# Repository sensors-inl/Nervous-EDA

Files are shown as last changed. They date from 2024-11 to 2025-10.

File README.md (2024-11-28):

<p align="center">
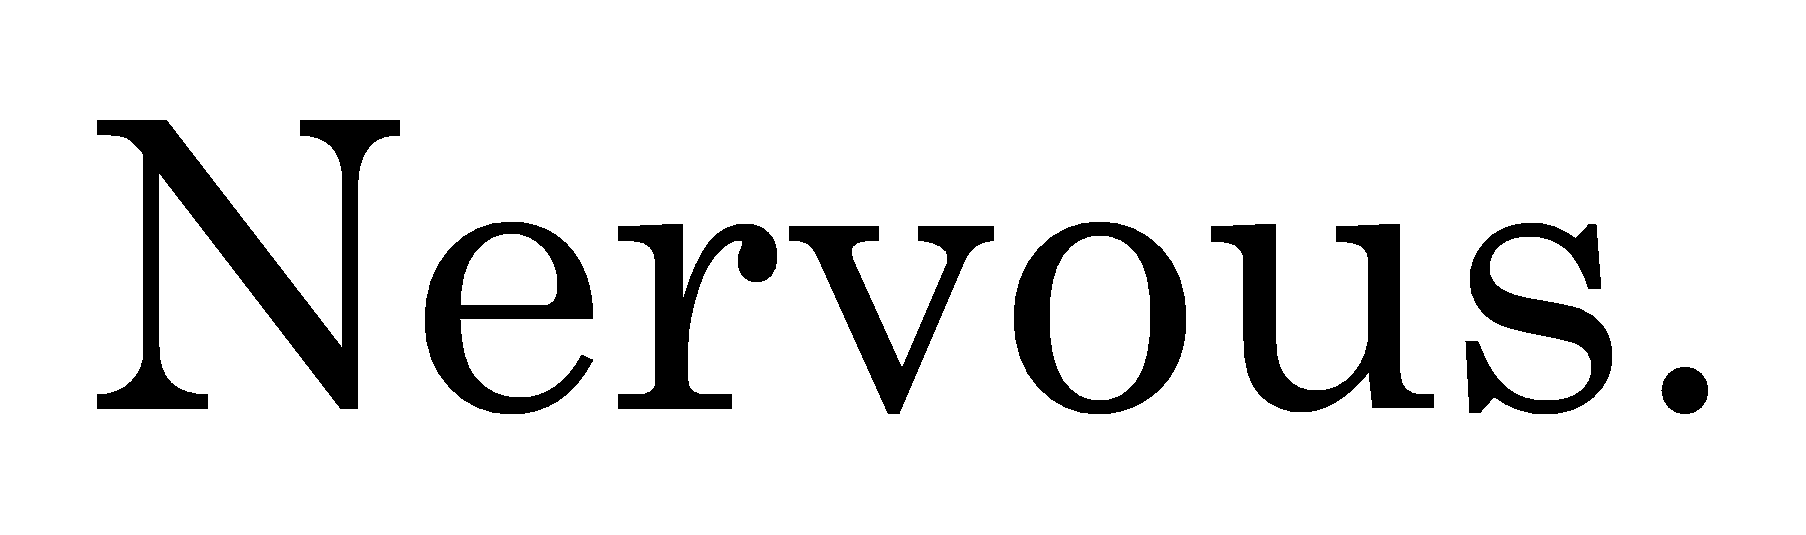
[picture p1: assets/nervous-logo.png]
    
</p>
<p align="center">
    <h1 align="center">Nervous EDA Sensor</h1>
</p>

<p align="center">
    
    
	
	
</p>

<p align="center">B. Massot, E. Desmazure, A. Montalibet, E. McAdams, and C. Gehin, "A Portable Device Performing Continuous Impedance Spectroscopy for Skin Conductivity," <i>IEEE Sensors Journal</i>, doi: <a href="https://doi.org/10.1109/JSEN.2024.3485187" target="_blank">10.1109/JSEN.2024.3485187</a>.</p>

## Table of Contents

- [Table of Contents](#table-of-contents)
- [Overview](#overview)
- [Features](#features)
- [Instructions](#instructions)
- [Releases](#releases)
- [Contributing](#contributing)
- [License](#license)
- [Acknowledgments](#acknowledgments)
- [Contact](#contact)

---

## Overview

The **Nervous** project is an initiative based on open-hardware and open-source principles, aimed at providing wearable sensors and software for analyzing the Autonomic Nervous System (ANS) activity.

The **Nervous EDA** project is part of the **[Nervous Toolkit](https://github.com/sensors-inl/Nervous-Toolkit)** and includes hardware design files and firmware source files for creating an electrodermal activity (EDA) sensor.
The device is wireless and transmits the collected data via Bluetooth Low Energy.

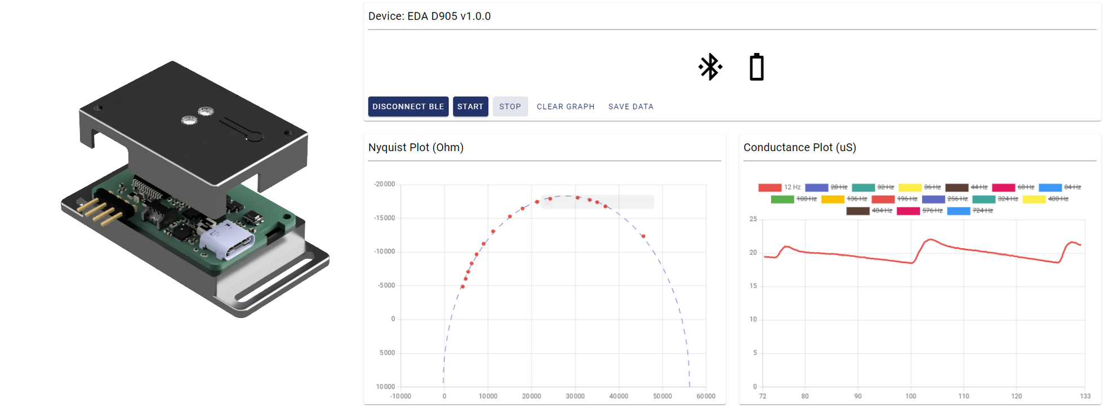
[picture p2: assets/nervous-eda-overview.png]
Illustration of the Nervous EDA sensor and real-time data shown on the application Nervous EDA sensor and application


This EDA sensor uses continuous multifrequency impedance spectroscopy to measure skin conductivity at 16 simultaneous frequencies with a rate of 8 spectra per second.
The method is fully described detailed in [B. Massot et al.](https://doi.org/10.1109/JSEN.2024.3485187).
The embedded electronic circuit employs two microcontrollers.
The first one is a PSoC Analog co-processor (Infineon) for analog signal generation and conditioning.
The second one is an ISP1807 (Insight SiP) which houses a nRF52840 (Nordic Semiconductor) for voltage and current sampling, impedance calculation and Bluetooth Low Energy communication.

---

## Features

This project is actually a collection of three sub-projects for the sensor design, located in the following directories:

[hardware](./hardware/): This folder contains ECAD files for producing PCBs and assembling circuits for a wireless wrist-worn EDA sensor.
A archive (.zip) containing the design and manufacturing/assembly files for the sensor is available in the releases of this project.

[firmware](./firmware/): This folder contains source files to build binaries for programming both microcontrollers.
Precompiled binaries are also provided in the releases of this project.

[web-app](./web-app/): While the sensor is primarily designed to work with the [```nervous-sensors```](https://github.com/sensors-inl/Nervous-Sensors) Python package included in the Nervous Toolkit, a standalone web application is provided for simplified use of the sensor.
It offers sensor control, real-time data visualization, and recording features.
Pre-built executables for both Microsoft Windows and Linux are also available in the releases of this project.

---

## Instructions

Detailed instructions are provided in each subdirectory for manufacturing, programming, and using the sensor.

---

## Releases

Each [release](https://github.com/sensors-inl/Nervous-ECG/releases/latest) contains built firmware and application binaries as well as an archive of ECAD files.

---

## Contributing

Contributions are what make the open-source community such a great place to learn, inspire, and create. Any contributions you make are greatly appreciated. You can open an issue to report a bug, request a feature, or submit a pull request.

We especially welcome contributions to port the nRF52 firmware from nRF5 SDK to nRF Connect SDK, which requires expertise with the `nrfx` library inside Zephyr.

---

## License

This project, along with the entire Nervous initiative, is licensed under the [MIT License](https://opensource.org/licenses/MIT). For more details, see the [License](LICENSE.md) file.

---

## Acknowledgments

The main contributors to this project are Bertrand Massot, Matthieu Mesnage, and Hugo Buy from INSA Lyon, CNRS, INL UMR 5270, Villeurbanne, France.

This work was supported by the **French National Research Agency (ANR)** under grant **ANR-22-CE31-0023-03 RENFORCE**.

---

## Contact

[bertrand.massot@insa-lyon.fr](mailto:bertrand.massot@insa-lyon.fr)

---

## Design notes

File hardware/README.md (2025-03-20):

<p align="center">
    <h1 align="center">Nervous EDA Hardware</h1>
</p>

<p align="center">
    <a href="https://www.kicad.org/">
        
    </a>
    <a href="https://opensource.org/licenses/MIT">
        
    </a>
</p>

## Table of Contents

- [Table of Contents](#table-of-contents)
- [Overview](#overview)
- [Hardware features](#hardware-features)
- [Manufacturing and assembling](#manufacturing-and-assembling)
  - [PCB properties for manufacturing](#pcb-properties-for-manufacturing)
- [Modification](#modification)
- [Casing](#casing)
- [Note on cables and electrodes placement](#note-on-cables-and-electrodes-placement)
- [Release](#release)

---

## Overview

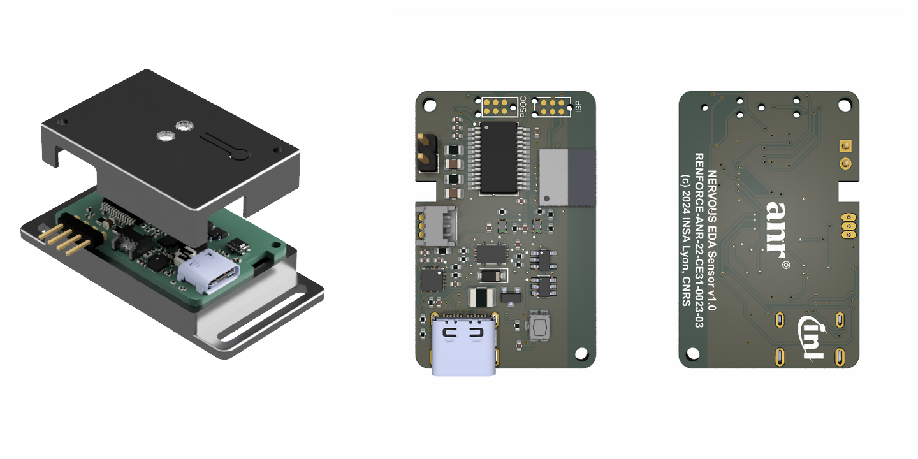
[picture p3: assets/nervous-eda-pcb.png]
Nervous EDA printed circuit board


This folder contains ECAD files for the production of PCBs and assembly of circuits for the Nervous EDA sensor.
The printed circuit board was designed using the open source electronics design automation suite [KiCad EDA](https://www.kicad.org/) v9.0.0

---

## Hardware features

- USB-C connector for charging the battery
- Embedded LiPo battery charger and I2C fuel gauge
- On/Off SPST button (enables/disables the voltage regulator)
- RGB status LED
- CY8C4A45PVI-481 Programmable-System-On-Chip for impedance spectroscopy
- nRF52840 (ISP1807) with Bluetooth Low Energy

---

## Manufacturing and assembling

The following files are available in the `Export` folder:

- **Export/Manufacturing**: contains Gerber (.gbr) and drill files (.drl)
- **Export/Assembly**: contains assembly drawing (.pdf), pick and place files (.pos), and BOM (.csv)

---

### PCB properties for manufacturing

Some PCB manufacturers may require the following properties. The table below summarizes the principal PCB properties:

| Property                    | Value              |
| --------------------------- | ------------------ |
| Dimensions                  | 21.5 mm x 33.5 mm  |
| Number of layers            | 2                  |
| Minimal insulation width    | 0.150 mm           |
| Minimal trace width         | 0.150 mm           |
| Minimal hole size           | 0.200 mm           |

---

## Modification

The `Source` folder contains the original KiCad project, created using KiCad version 7.0.8.

---

## Casing

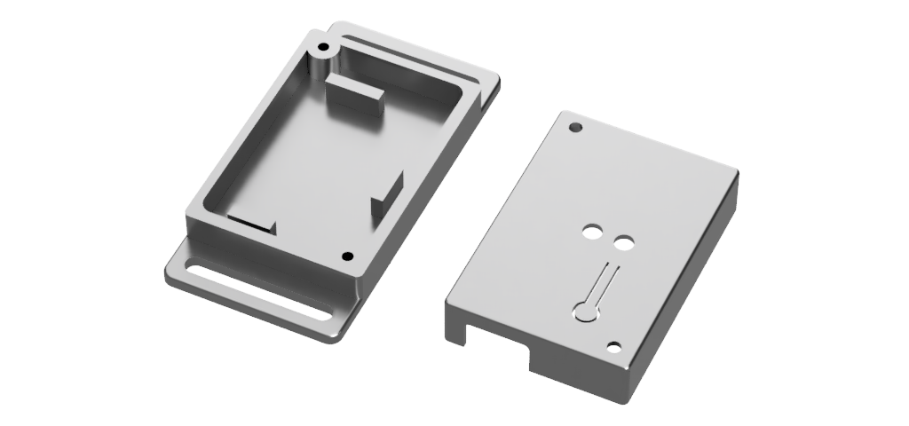
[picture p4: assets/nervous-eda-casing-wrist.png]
Nervous EDA casing for wrist attachment


Several 3D models are available for producing a casing for the electronics. STEP and STL files are located in the `Casing` folder:

- **casing_top** and **casing_bottom** are two parts that assemble together with two M2 screws, where the PCB and a 150 mAh LiPo battery fit. A specially designed battery compartment ensures that it does not overlap with the antenna of the ISAP1807 chip located on the longitudinal edge of the PCB. The design of the bottom part includes handles for wrist attachment.
- **casing_bottom_controller** is a modified version of the bottom part, designed to mount the electronics circuit and battery onto a Valve Index controller for ECG assessment during virtual environment sessions.

---

## Note on cables and electrodes placement

This sensor is designed to capture skin conductivity across two electrodes.
For connectivity, we implemented a simple 2.54 mm, 2-way header on the sensor, allowing for custom electrode connections.
It's advised to use short cables for connecting the two electrodes in proximity to the device.

We recommend using solid-gel electrodes such as Ambu&reg; WhiteSensor 40713 with an initial wear period of 10 minutes before starting measurements.
We constructed cables featuring female crimp terminals on the sensor end and 3 mm banana plugs with a snap adapter on the electrode end.
Finally, securely hold the electrodes in place, along with the cables near the electrodes, using medical tape to minimize noise from connector friction.

---

## Release

The entire folder is provided as an archive (`Nervous-EDA-hardware-vX.X.X.zip`) in the [releases](https://github.com/sensors-inl/Nervous-EDA/releases/latest) of this project.

---

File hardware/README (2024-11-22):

<p align="center">
    <h1 align="center">Nervous EDA Hardware</h1>
</p>

<p align="center">
    <a href="https://www.kicad.org/">
        
    </a>
    <a href="https://opensource.org/licenses/MIT">
        
    </a>
</p>

## Table of Contents

- [Table of Contents](#table-of-contents)
- [Overview](#overview)
- [Hardware features](#hardware-features)
- [Manufacturing and assembling](#manufacturing-and-assembling)
  - [PCB properties for manufacturing](#pcb-properties-for-manufacturing)
- [Modification](#modification)
- [Casing](#casing)
- [Note on cables and electrodes placement](#note-on-cables-and-electrodes-placement)
- [Release](#release)
- [Contributing](#contributing)
- [Contact](#contact)
- [License](#license)
- [Acknowledgments](#acknowledgments)

---

## Overview

This folder contains ECAD files for the production of PCBs and assembly of circuits for the Nervous EDA sensor.
The printed circuit board was designed using the open source electronics design automation suite [KiCad EDA](https://www.kicad.org/) v7.0.8

---

## Hardware features

- USB-C connector for charging the battery
- Embedded LiPo battery charger and I2C fuel gauge
- On/Off SPST button (enables/disables the voltage regulator)
- RGB status LED
- CY8C4A45PVI-481 Programmable-System-On-Chip for impedance spectroscopy
- nRF52840 (ISP1807) with Bluetooth Low Energy

---

## Manufacturing and assembling

The following files are available in the `Export` folder:

- **Export/Manufacturing**: contains Gerber (.gbr) and drill files (.drl)
- **Export/Assembly**: contains assembly drawing (.pdf), pick and place files (.pos), and BOM (.csv)

---

### PCB properties for manufacturing

Some PCB manufacturers may require the following properties. The table below summarizes the principal PCB properties:

| Property                    | Value              |
| --------------------------- | ------------------ |
| Dimensions                  | 21.5 mm x 33.5 mm  |
| Number of layers            | 2                  |
| Minimal insulation width    | 0.150 mm           |
| Minimal trace width         | 0.150 mm           |
| Minimal hole size           | 0.200 mm           |

---

## Modification

The `Source` folder contains the original KiCad project, created using KiCad version 7.0.8.

---

## Casing

Nervous ECG casing for wrist attachment

Several 3D models are available for producing a casing for the electronics. STEP and STL files are located in the `Casing` folder:

- **casing_top** and **casing_bottom** are two parts that assemble together with two M2 screws, where the PCB and a 150 mAh LiPo battery fit. A specially designed battery compartment ensures that it does not overlap with the antenna of the ISAP1807 chip located on the longitudinal edge of the PCB. The design of the bottom part includes handles for wrist attachment.
- **casing_bottom_controller** is a modified version of the bottom part, designed to mount the electronics circuit and battery onto a Valve Index controller for ECG assessment during virtual environment sessions.

---

## Note on cables and electrodes placement

This sensor is designed to capture skin conductivity across two electrodes.
For connectivity, we implemented a simple 2.54 mm, 2-way header on the sensor, allowing for custom electrode connections.
It's advised to use short cables for connecting the two electrodes in proximity to the device.

We recommend using solid-gel electrodes such as Ambu&reg; WhiteSensor 40713 with an initial wear period of 10 minutes before starting measurements.
We constructed cables featuring female crimp terminals on the sensor end and 3 mm banana plugs with a snap adapter on the electrode end.
Finally, securely hold the electrodes in place, along with the cables near the electrodes, using medical tape to minimize noise from connector friction.

---

## Release

The entire folder is provided as an archive (`Nervous-EDA-hardware-vX.X.X.zip`) in the [releases](https://github.com/sensors-inl/Nervous-EDA/releases/latest) of this project.

---

## Contributing

Contributions are what make the open-source community great. Any contributions are greatly appreciated. You can open an issue to report a bug, request a feature, or submit a pull request.

---

## Contact

**Bertrand MASSOT**  
[bertrand.massot@insa-lyon.fr](mailto:bertrand.massot@insa-lyon.fr)

---

## License

This project, along with the entire Nervous initiative, is licensed under the [MIT License](https://opensource.org/licenses/MIT). For more details, see the [License](LICENSE.md) file.

---

## Acknowledgments

The main contributors to this project are  Bertrand Massot, Matthieu Mesnage, and Hugo Buy from INSA Lyon, CNRS, INL UMR 5270, Villeurbanne, France.

This work was supported by the **French National Research Agency (ANR)** under grant **ANR-22-CE31-0023-03 RENFORCE**.

---

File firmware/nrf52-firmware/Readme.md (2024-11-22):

# RENFORCE EDA firmware

## Description
This project contains the firmware for the EDA Sensors of Franch ANR project RENFORCE.
The firmware targets nRF52 microcontrolers family and is developed upon nRF5 SDK 17.0.2.
Currently the nRF52840 together with s140_nrf52_7.2.0_softdevice.hex SoftDevice are used.

## Objectives

This code controls a custom analog frontend and acquires voltage and current signals from the frontend.
The frontend generate a current by using IDACs controlled with a software waveform.
This waveform contains multiple frequencies, and the absolute frequencies depend on the sampling rate, which is controlled by a clock which is provided in this code.
Current signal is actually converted by the frontend to a voltage signal by a TIA.

The device aims at :
- Measuring skin admittance in real-time over multiple frequencies from voltage/current signals, and send real / imaginary values of admittance (conductance / susceptance).
- Detecting electrodermal responses and physiological events.
- Being low-power!
- Being small ...

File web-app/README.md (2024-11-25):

<p align="center">
    <h1  align="center">Nervous EDA Application</h1>
</p>

<p align="center">
    
    
    <a href="https://opensource.org/licenses/MIT">
        
    </a>
</p>

## Table of Contents

- [Table of Contents](#table-of-contents)
- [Overview](#overview)
- [Usage](#usage)
- [Building Executable Binaries for Windows and Linux](#building-executable-binaries-for-windows-and-linux)
  - [Prerequisites](#prerequisites)
  - [Build Instructions](#build-instructions)
- [Release](#release)

---

## Overview

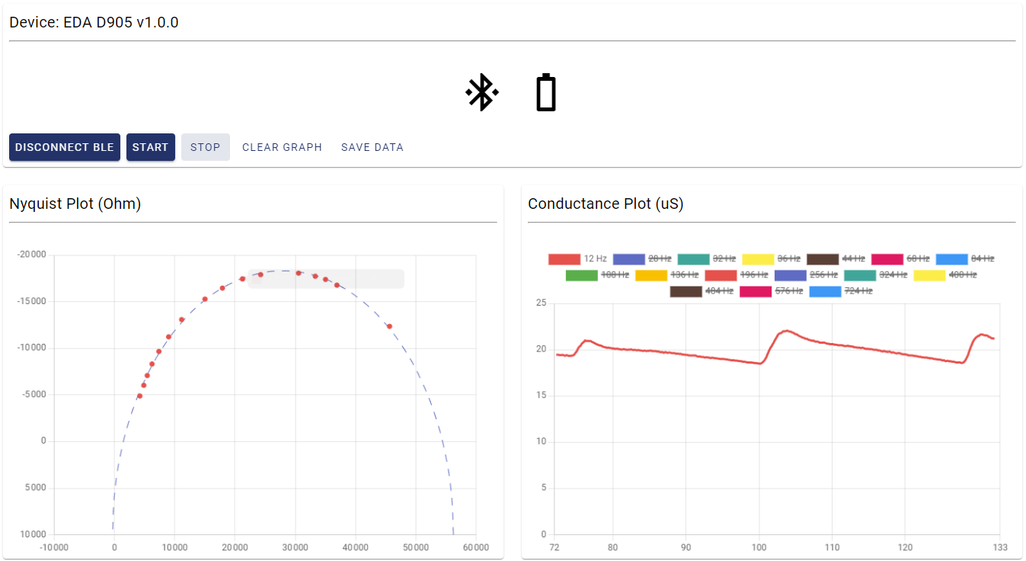
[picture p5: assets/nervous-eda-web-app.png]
Web application of the Nervous EDA sensor Web application of the Nervous ECG sensor


This repository contains an HTML/JavaScript application that connects to Nervous EDA sensors. The application provides real-time Nyquist plot of the impedance spectroscopy
with simple fit of the data using a circular model. The application also plots impedance modulus for each of the 16 frequencies acquired. It can saves data to a `.csv` file. It consists of a single static HTML page, `index.html`, along with two JavaScript files: `app.js` (the main application script) and `proto.js` (the JavaScript compilation of the Protocol Buffer files).

This application uses several libraries. For offline usage, local copies of these libraries are included. The following versions of the libraries are currently used:

- [**Chart.js**](https://www.chartjs.org/) (v4.4.0)
- [**google-protobuf**](https://www.npmjs.com/package/google-protobuf) (v3.19.0)
- [**hammerjs**](https://hammerjs.github.io/) (v2.0.8)
- [**jsxgraph**](https://jsxgraph.uni-bayreuth.de/wp/index.html) (v1.3.2)
- [**material-components-web**](https://www.npmjs.com/package/material-components-web) (v14.0.0)
- [**cobs**](https://www.npmjs.com/package/cobs) (v0.2.1)

Additional configuration files, such as `forge.config.js`, `jsconfig.json`, `main.js`, and `package.js`, are provided to facilitate building the application into an executable using [**Electron**](https://www.electronjs.org/) and [**Electron Forge**](https://www.electronforge.io/). This allows you to build executables for Windows and Linux by following the instructions below.

---

## Usage

To use the application, simply open `index.html` in a Chromium-based web browser (e.g., Chrome, Microsoft Edge). 

1. Press the **CONNECT** button to scan for available ECG sensors.
2. Once connected, press the **START** button to begin collecting and plotting data in real-time.
3. Press the **STOP** button to stop the data collection and save the data to a `.csv` file.

Since the application runs in the web browser, the `.csv` file will be automatically downloaded, but the entire application runs locally in the browser.

> **Note:** When using the built executable (see below), the application will automatically connect to the first available sensor rather than displaying a list of available sensors.

---

## Building Executable Binaries for Windows and Linux

This application can be built into executables for Windows and Linux using Electron.

### Prerequisites

Before building the application, the following dependencies must be installed:

- [Node.js and npm](https://docs.npmjs.com/downloading-and-installing-node-js-and-npm) (required to install and use Electron and Electron Forge)
- Install Electron: `npm install --save-dev electron`
- Install Electron Forge: `npm install --save-dev @electron-forge/cli`

### Build Instructions

1. Prepare the build environment:

    ```console
    npx electron-forge import
    ```

2. Package the build, specifying the architecture and OS. For example, for Windows, use:

    ```console
    npx electron-forge package --arch=x64 --platform=win32
    ```

    For Linux, use:

    ```console
    npx electron-forge package --arch=x64 --platform=linux
    ```

3. The packaged binaries will be located in the `out/` directory.

---

## Release

Executable binaries for Windows and Linux are automatically built in CI and are available for download as `.zip` archives from each [release](https://github.com/sensors-inl/Nervous-EDA/releases/latest).

---

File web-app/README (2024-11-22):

<p align="center">
    <h1  align="center">Nervous EDA Application</h1>
</p>

<p align="center">
    
    
    <a href="https://opensource.org/licenses/MIT">
        
    </a>
</p>

## Table of Contents

- [Table of Contents](#table-of-contents)
- [Overview](#overview)
- [Usage](#usage)
- [Building Executable Binaries for Windows and Linux](#building-executable-binaries-for-windows-and-linux)
  - [Prerequisites](#prerequisites)
  - [Build Instructions](#build-instructions)
- [Release](#release)
- [Contributing](#contributing)
- [Contact](#contact)
- [License](#license)
- [Acknowledgments](#acknowledgments)

---

## Overview

Web application of the Nervous EDA sensor Web application of the Nervous ECG sensor

This repository contains an HTML/JavaScript application that connects to Nervous EDA sensors. The application provides real-time Nyquist plot of the impedance spectroscopy
with simple fit of the data using a circular model. The application also plots impedance modulus for each of the 16 frequencies acquired. It can saves data to a `.csv` file. It consists of a single static HTML page, `index.html`, along with two JavaScript files: `app.js` (the main application script) and `proto.js` (the JavaScript compilation of the Protocol Buffer files).

This application uses several libraries. For offline usage, local copies of these libraries are included. The following versions of the libraries are currently used:

- [**Chart.js**](https://www.chartjs.org/) (v4.4.0)
- [**google-protobuf**](https://www.npmjs.com/package/google-protobuf) (v3.19.0)
- [**hammerjs**](https://hammerjs.github.io/) (v2.0.8)
- [**jsxgraph**](https://jsxgraph.uni-bayreuth.de/wp/index.html) (v1.3.2)
- [**material-components-web**](https://www.npmjs.com/package/material-components-web) (v14.0.0)
- [**cobs**](https://www.npmjs.com/package/cobs) (v0.2.1)

Additional configuration files, such as `forge.config.js`, `jsconfig.json`, `main.js`, and `package.js`, are provided to facilitate building the application into an executable using [**Electron**](https://www.electronjs.org/) and [**Electron Forge**](https://www.electronforge.io/). This allows you to build executables for Windows and Linux by following the instructions below.

---

## Usage

To use the application, simply open `index.html` in a Chromium-based web browser (e.g., Chrome, Microsoft Edge). 

1. Press the **CONNECT** button to scan for available ECG sensors.
2. Once connected, press the **START** button to begin collecting and plotting data in real-time.
3. Press the **STOP** button to stop the data collection and save the data to a `.csv` file.

Since the application runs in the web browser, the `.csv` file will be automatically downloaded, but the entire application runs locally in the browser.

> **Note:** When using the built executable (see below), the application will automatically connect to the first available sensor rather than displaying a list of available sensors.

---

## Building Executable Binaries for Windows and Linux

This application can be built into executables for Windows and Linux using Electron.

### Prerequisites

Before building the application, the following dependencies must be installed:

- [Node.js and npm](https://docs.npmjs.com/downloading-and-installing-node-js-and-npm) (required to install and use Electron and Electron Forge)
- Install Electron: `npm install --save-dev electron`
- Install Electron Forge: `npm install --save-dev @electron-forge/cli`

### Build Instructions

1. Prepare the build environment:

    ```console
    npx electron-forge import
    ```

2. Package the build, specifying the architecture and OS. For example, for Windows, use:

    ```console
    npx electron-forge package --arch=x64 --platform=win32
    ```

    For Linux, use:

    ```console
    npx electron-forge package --arch=x64 --platform=linux
    ```

3. The packaged binaries will be located in the `out/` directory.

---

## Release

Executable binaries for Windows and Linux are automatically built in CI and are available for download as `.zip` archives from each [release](https://github.com/sensors-inl/Nervous-EDA/releases/latest).

---

## Contributing

Contributions are what make the open-source community a great place to learn, inspire, and create. Any contributions you make are greatly appreciated. You can open an issue to report a bug, request a feature, or submit a pull request.

---

## Contact

**Bertrand MASSOT**  
Email: [bertrand.massot@insa-lyon.fr](mailto:bertrand.massot@insa-lyon.fr)

---

## License

This project, as part of the Nervous initiative, is licensed under the [MIT License](https://opensource.org/licenses/MIT). For more details, refer to the [LICENSE](LICENSE.md) file.

---

## Acknowledgments

The primary contributor to this project is **Bertrand Massot** from INSA Lyon, CNRS, INL UMR 5270, Villeurbanne, France.

This work was supported by the **French National Research Agency (ANR)** under grant **ANR-22-CE31-0023-03 RENFORCE**.

---

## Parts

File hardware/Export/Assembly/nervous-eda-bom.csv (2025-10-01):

Reference | Value | Qty | Manufacturer | Manufacturer Part Number | Supplier | Supplier Part Number
BT1 | BATT LI-PO 3.7V 165MAH | 1 | BAK TECHNOLOGY | LP-402025-1S-3 | FARNELL | 2077885
C1,C2,C6,C7,C8,C12,C13 | CAP CER 1UF 10V X5R 0402 | 7 | Yageo | CC0402KRX5R6BB105 | Farnell | 1458896
C3,C4 | CAP CER 4.7UF 6.3V X5R 0402 | 2 | Yageo | CC0402KRX5R5BB475 | Farnell | 3369135
C5 | CAP CER 0.47UF 10V X5R 0402 | 1 | Yageo | CC0402KRX5R6BB474 | Farnell | 3369138
C9,C10,C11,C14 | CAP CER 0.1UF 16V X7R 0402 | 4 | Yageo | CC0402JRX7R7BB104 | Farnell | 3369125
D1 | DIODE SCHOTTKY 20V 500MA SOD123 | 1 | STMicroelectronics | STPS0520Z | FARNELL | 1467545
D4,D5 | LED RGB CLEAR 4SMD | 2 | KINGBRIGHT | APHF1608LSEEQBDZGKC | DIGIKEY | 754-2143-1-ND
F1 | PTC RESET FUSE 16V 500MA 1210 | 1 | BEL | 0ZCH0050FF2G | Farnell | 2848519
J1 | CONN RCP USB3.1 TYPEC 24P SMD RA | 1 | MOLEX | 105450-0101 | FARNELL | 2524076
J2 | MOLEX 53048-0310 | 1 | MOLEX | 53048-0310 | FARNELL | 9732918
J4 | CONN HEADER R/A 4POS 2.54MM | 1 | AMPHENOL COMMUNICATIONS SOLUTIONS | 77315-118-04LF | FARNELL | 3728851
R1 | RES SMD 3K OHM 1% 1/16W 0402 | 1 | Yageo | AC0402FR-073KL | Farnell | 3951323
R2,R4 | RES 5.1K OHM 0.5% 1/10W 0402 | 2 | PANASONIC | ERJ-U2RD5101X | FARNELL | 3516311
R3 | RES 5.9K OHM 1% 1/16W 0402 | 1 | Yageo | RC0402FR-075K9L | Farnell | 3951010
R5,R9,R10,R11,R13,R14 | RES 10K OHM 1% 1/16W 0402 | 6 | Yageo | RC0402FR-0710KL | Farnell | 9239359
R6,R7,R17 | RES 1K OHM 1% 1/16W 0402 | 3 | Yageo | RC0402FR-071KL | Farnell | 9239235
R8,R19 | RES 4.7K OHM 1% 1/16W 0402 | 2 | Yageo | RC0402FR-074K7L | Farnell | 9239316
R12 | RES 0.01 OHM 1% 1/10W 0603 | 1 | Yageo | RL0603FR-070R01L | Farnell | 8067767
R15 | RES Thick Film, 220kΩ, 1%, 0.125W, 100ppm/°C, 0805 | 1 | Yageo | RC0805FR-07220KL | Mouser | 603-RC0805FR-07220KL
U1 | SWITCH TACTILE SPST-NO 0.02A 15V | 1 | PANASONIC | EVP-AA502W | FARNELL | 2831733
U2 | TVS Diode WE-TVS-Standard, VRWM=5.0V | 1 | SEMTECH | SM05.TCT | Farnell | 1456392
U3 | IC INTFACE SPECIALIZED TSOT23-6 | 1 | ANALOG DEVICES | MAX16054AZT+T | FARNELL | 2515822
U4 | IC BATT CHG LI-ION 1CELL 16QFN | 1 | TEXAS INSTRUMENTS | BQ24074RGTT | FARNELL | 3123775
U5 | IC REG LINEAR 3.3V 200MA SOT23-5 | 1 | TEXAS INSTRUMENTS | TPS7A0533PDBVR | DIGIKEY | 296-TPS7A0533PDBVRDKR-ND
U6 | IC BATT FUEL GAUGE LICOO2 12SON | 1 | TEXAS INSTRUMENTS | BQ27441DRZR-G1A | FARNELL | 3123775
U7 | RF TXRX MODULE BT TRACE ANT SMD | 1 | INSIGHT SIP | ISP1807-LR-RS | DIGIKEY | 1786-1019-1-ND
U10 | IC MCU 32BIT 32KB FLASH 28SSOP | 1 | Infineon | CY8C4A45PVI-481 | Digi-Key | 448-CY8C4A45PVI-481-ND
U11,U12 | LIGHTPIPE PNL MT CONVEX 0.250" | 2 | DIALIGHT | 515-1302-0250F | FARNELL | 3775816

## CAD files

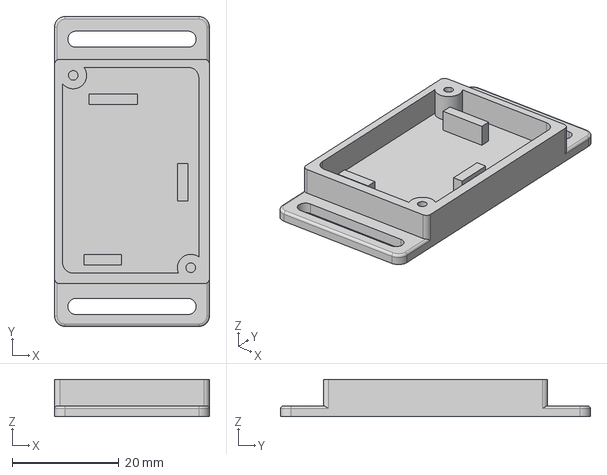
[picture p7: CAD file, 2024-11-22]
hardware/Casing/casing_bottom.step
29.0 x 58.0 x 7.00 mm

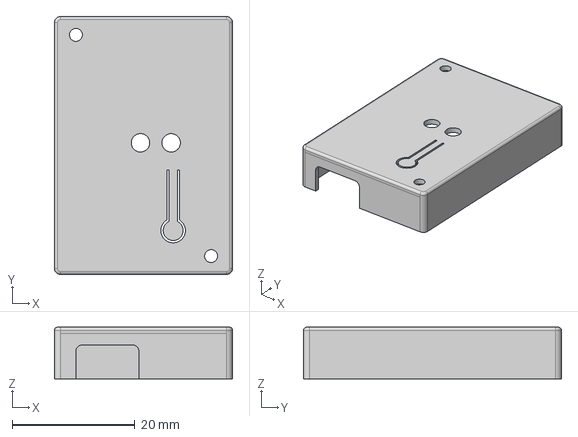
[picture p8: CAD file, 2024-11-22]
hardware/Casing/casing_top.step
29.0 x 42.0 x 8.40 mm

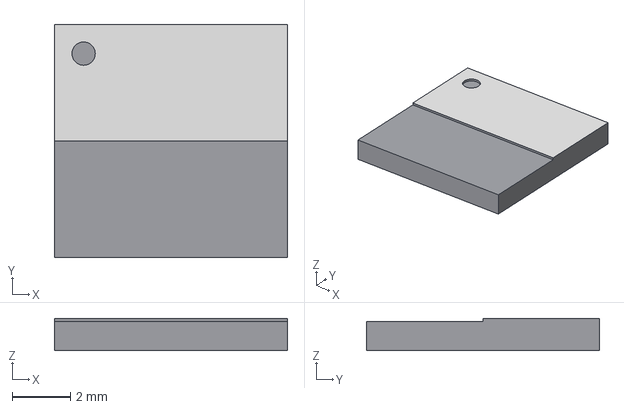
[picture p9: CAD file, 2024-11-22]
hardware/Source/nervous-eda-3dmodels/ISP1807-LR.step
8.00 x 8.00 x 1.10 mm

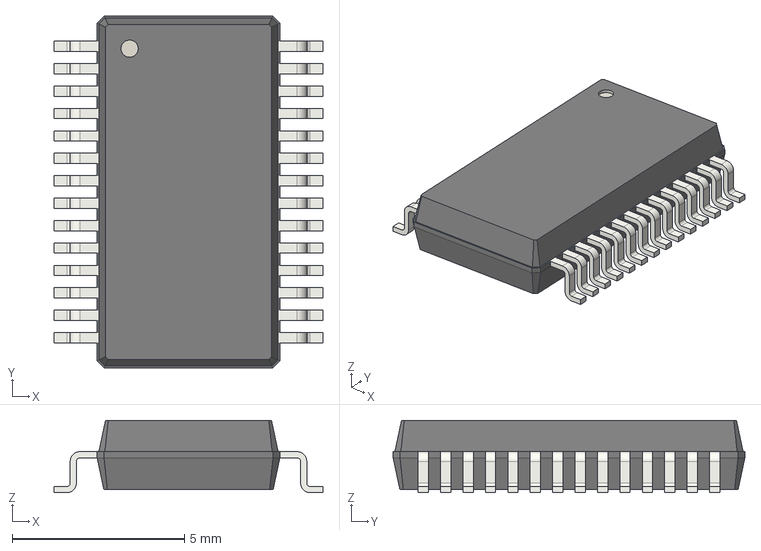
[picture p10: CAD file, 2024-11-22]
hardware/Source/nervous-eda-3dmodels/CY8C4A45PVI-481.step
7.80 x 10.2 x 2.10 mm

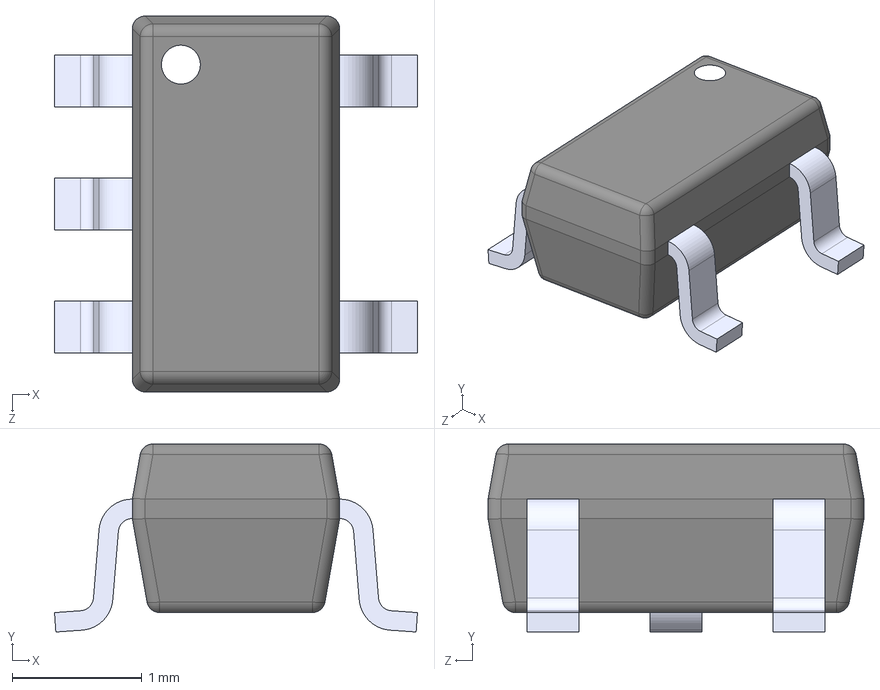
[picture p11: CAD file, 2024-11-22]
hardware/Source/nervous-eda-3dmodels/TPS7A0533PDBVR.step
2.80 x 1.45 x 2.90 mm

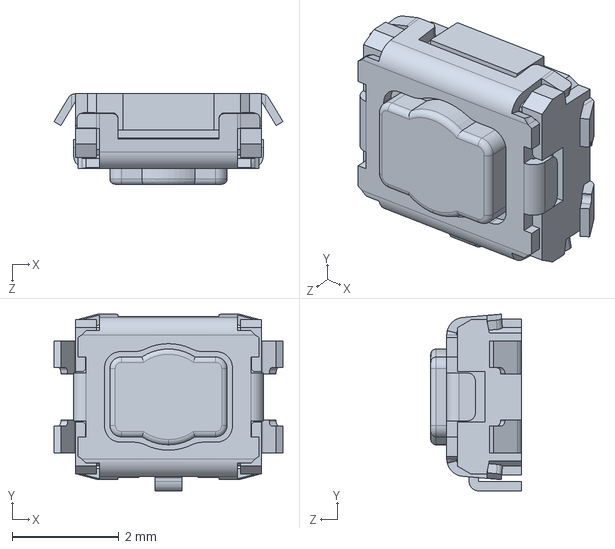
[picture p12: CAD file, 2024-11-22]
hardware/Source/nervous-eda-3dmodels/EVPAA-102K_302K_502W_702W_902Q.STEP
4.30 x 3.32 x 1.70 mm

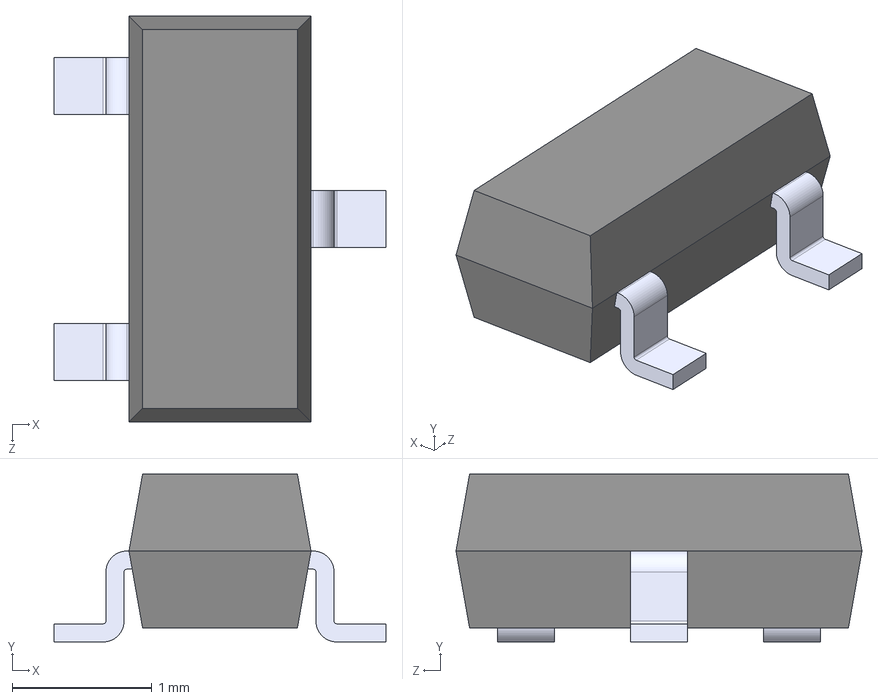
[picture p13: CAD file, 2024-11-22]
hardware/Source/nervous-eda-3dmodels/SM05.TCT.STEP
2.37 x 1.20 x 2.90 mm

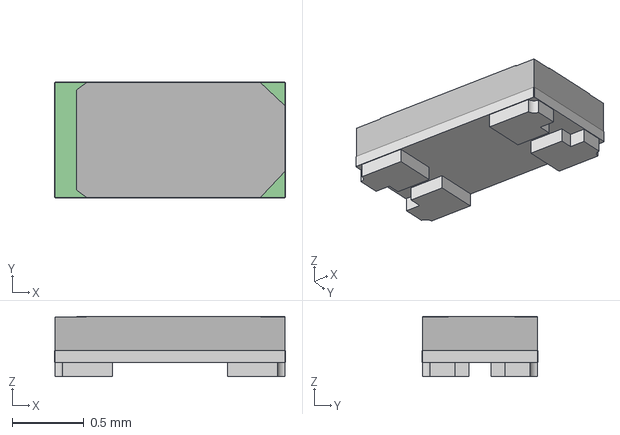
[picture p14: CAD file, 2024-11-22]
hardware/Source/nervous-eda-3dmodels/LED_RGB_SMD_0603.step
1.61 x 0.81 x 0.42 mm

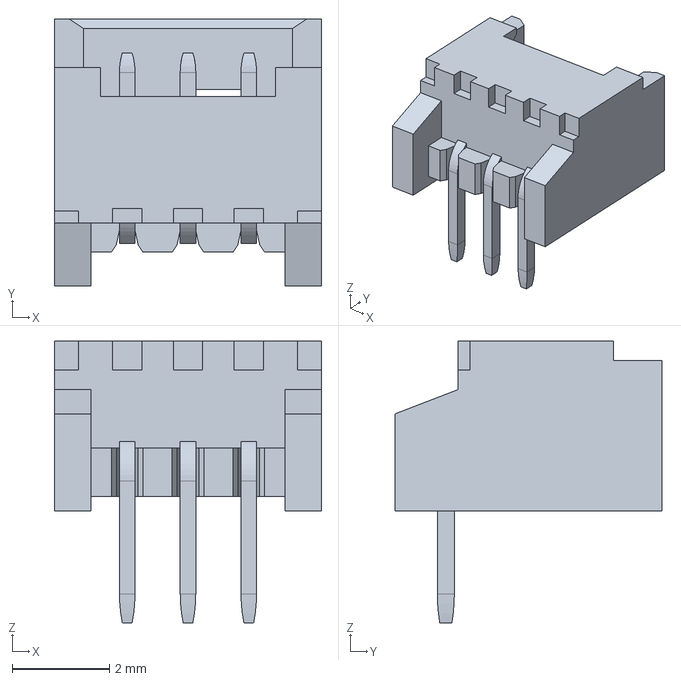
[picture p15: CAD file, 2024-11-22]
hardware/Source/nervous-eda-3dmodels/53048-0310.step
5.50 x 5.50 x 5.80 mm

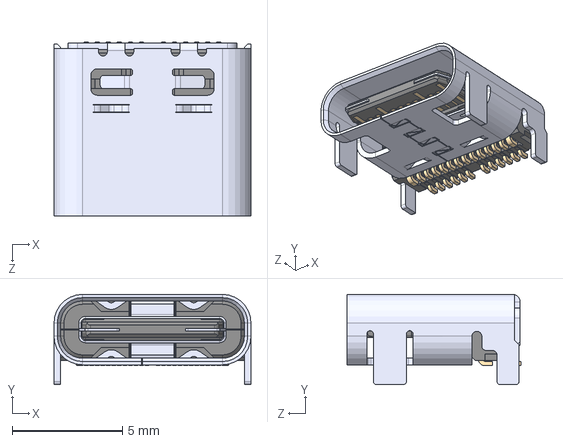
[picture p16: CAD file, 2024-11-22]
hardware/Source/nervous-eda-3dmodels/105450-0101.step
8.94 x 4.10 x 7.90 mm

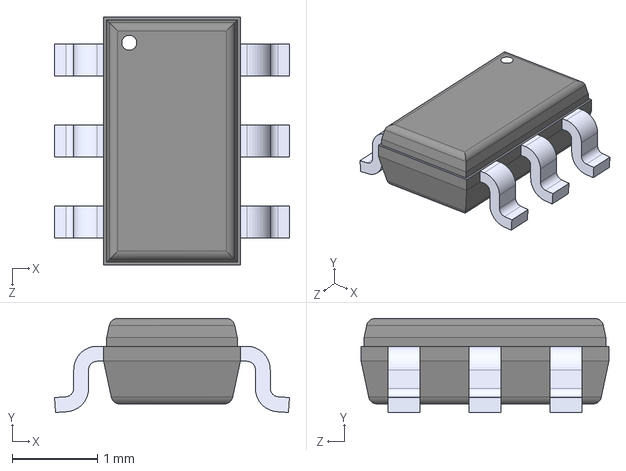
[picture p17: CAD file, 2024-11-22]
hardware/Source/nervous-eda-3dmodels/MAX16054AZT+T.STEP
2.75 x 1.10 x 2.90 mm

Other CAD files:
hardware/Casing/casing_bottom.stl
hardware/Casing/casing_top.stl

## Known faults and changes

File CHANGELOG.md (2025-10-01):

# Changelog

## [1.1.2] - 2025-10-01

### Hardware

- JTAG connectors footprint and designator update

### Software - web

- Add device name in exported CSV file
- Add secondary history chart for 724 Hz

## [1.1.1] - 2025-03-20

### Hardware

- Bump KiCad to version 9.0.0
- Adjust decoupling capacitors positioning

## [1.1.0] - 2025-02-15

- Use 32.768kHz clock instead of CPU clock for signal generation and sampling. This is much more precise to obtain the 4096 Hz sampling rate
- Apply a correction factor on phase for each frequency to compensate for DAC/ADC delay. This significantly reduces error on real on imaginary parts

## [1.0.0] - 2024-11-25

🎉 _First release !_

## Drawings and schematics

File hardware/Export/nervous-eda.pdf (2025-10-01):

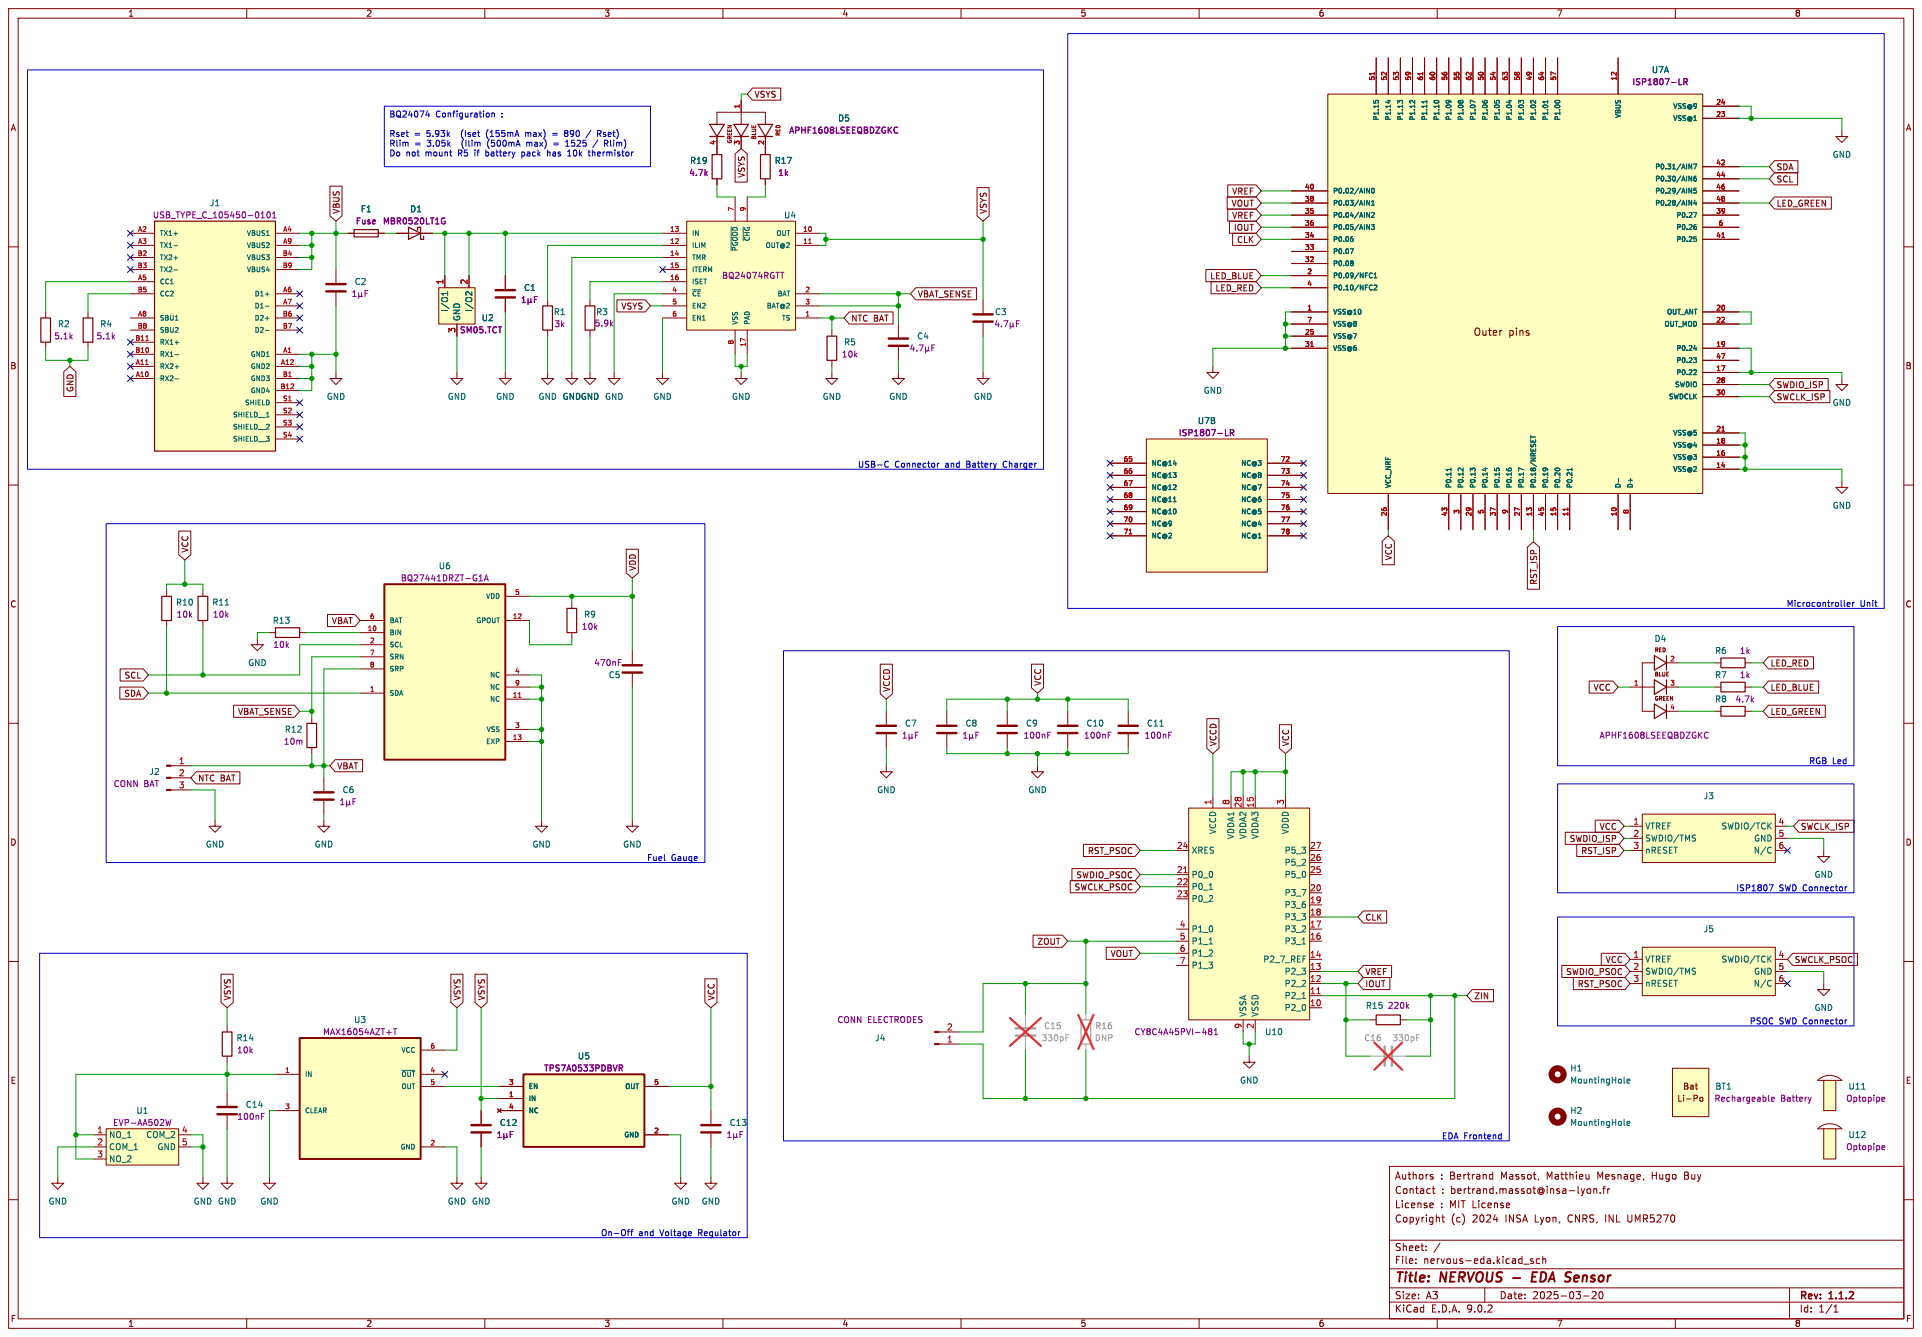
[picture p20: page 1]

IOUT VREF CLK VBUS

8 ~{CHG} 9 PAD 17 OUT 10 OUT@2 11 BAT 2 BAT@2 3 TS 1 U4 BQ24074RGTT GND

ISP1807 SWD Connector EDA Frontend

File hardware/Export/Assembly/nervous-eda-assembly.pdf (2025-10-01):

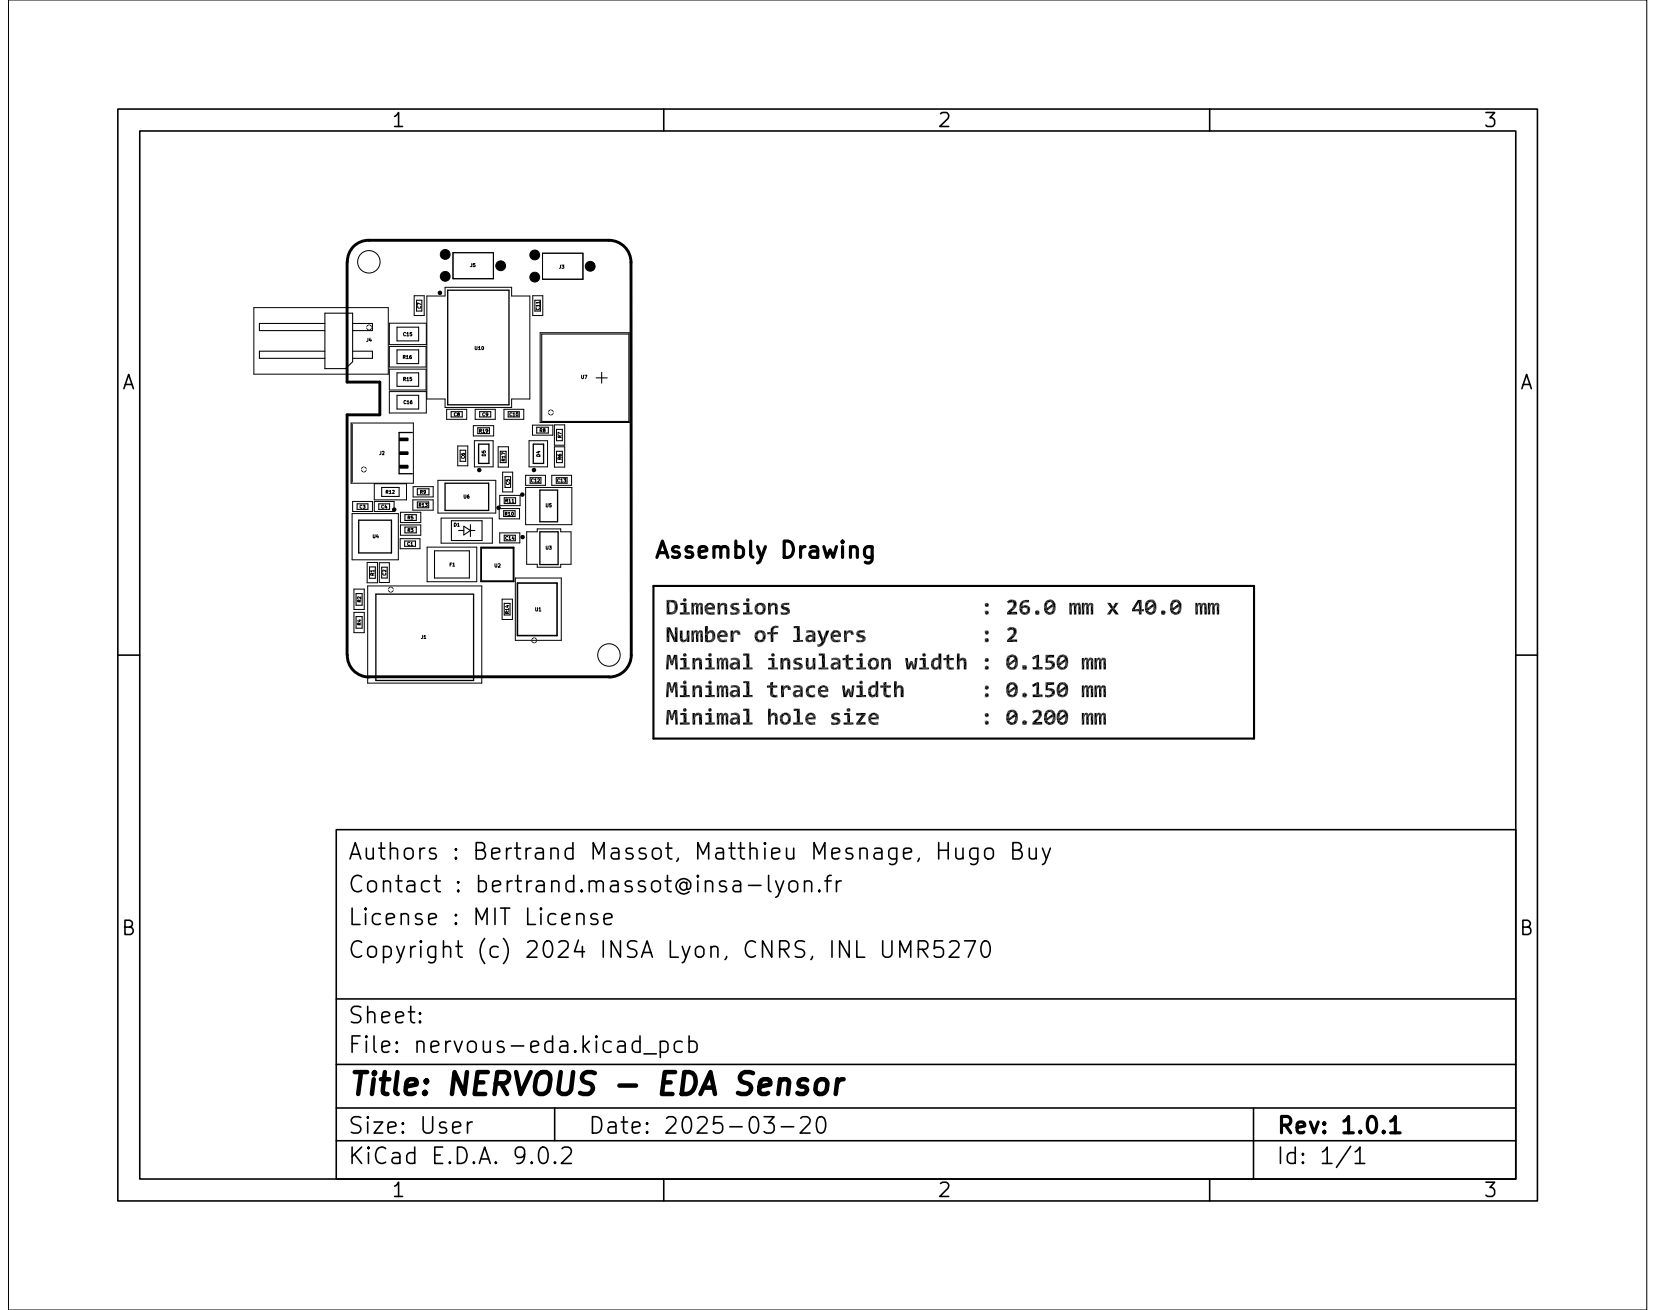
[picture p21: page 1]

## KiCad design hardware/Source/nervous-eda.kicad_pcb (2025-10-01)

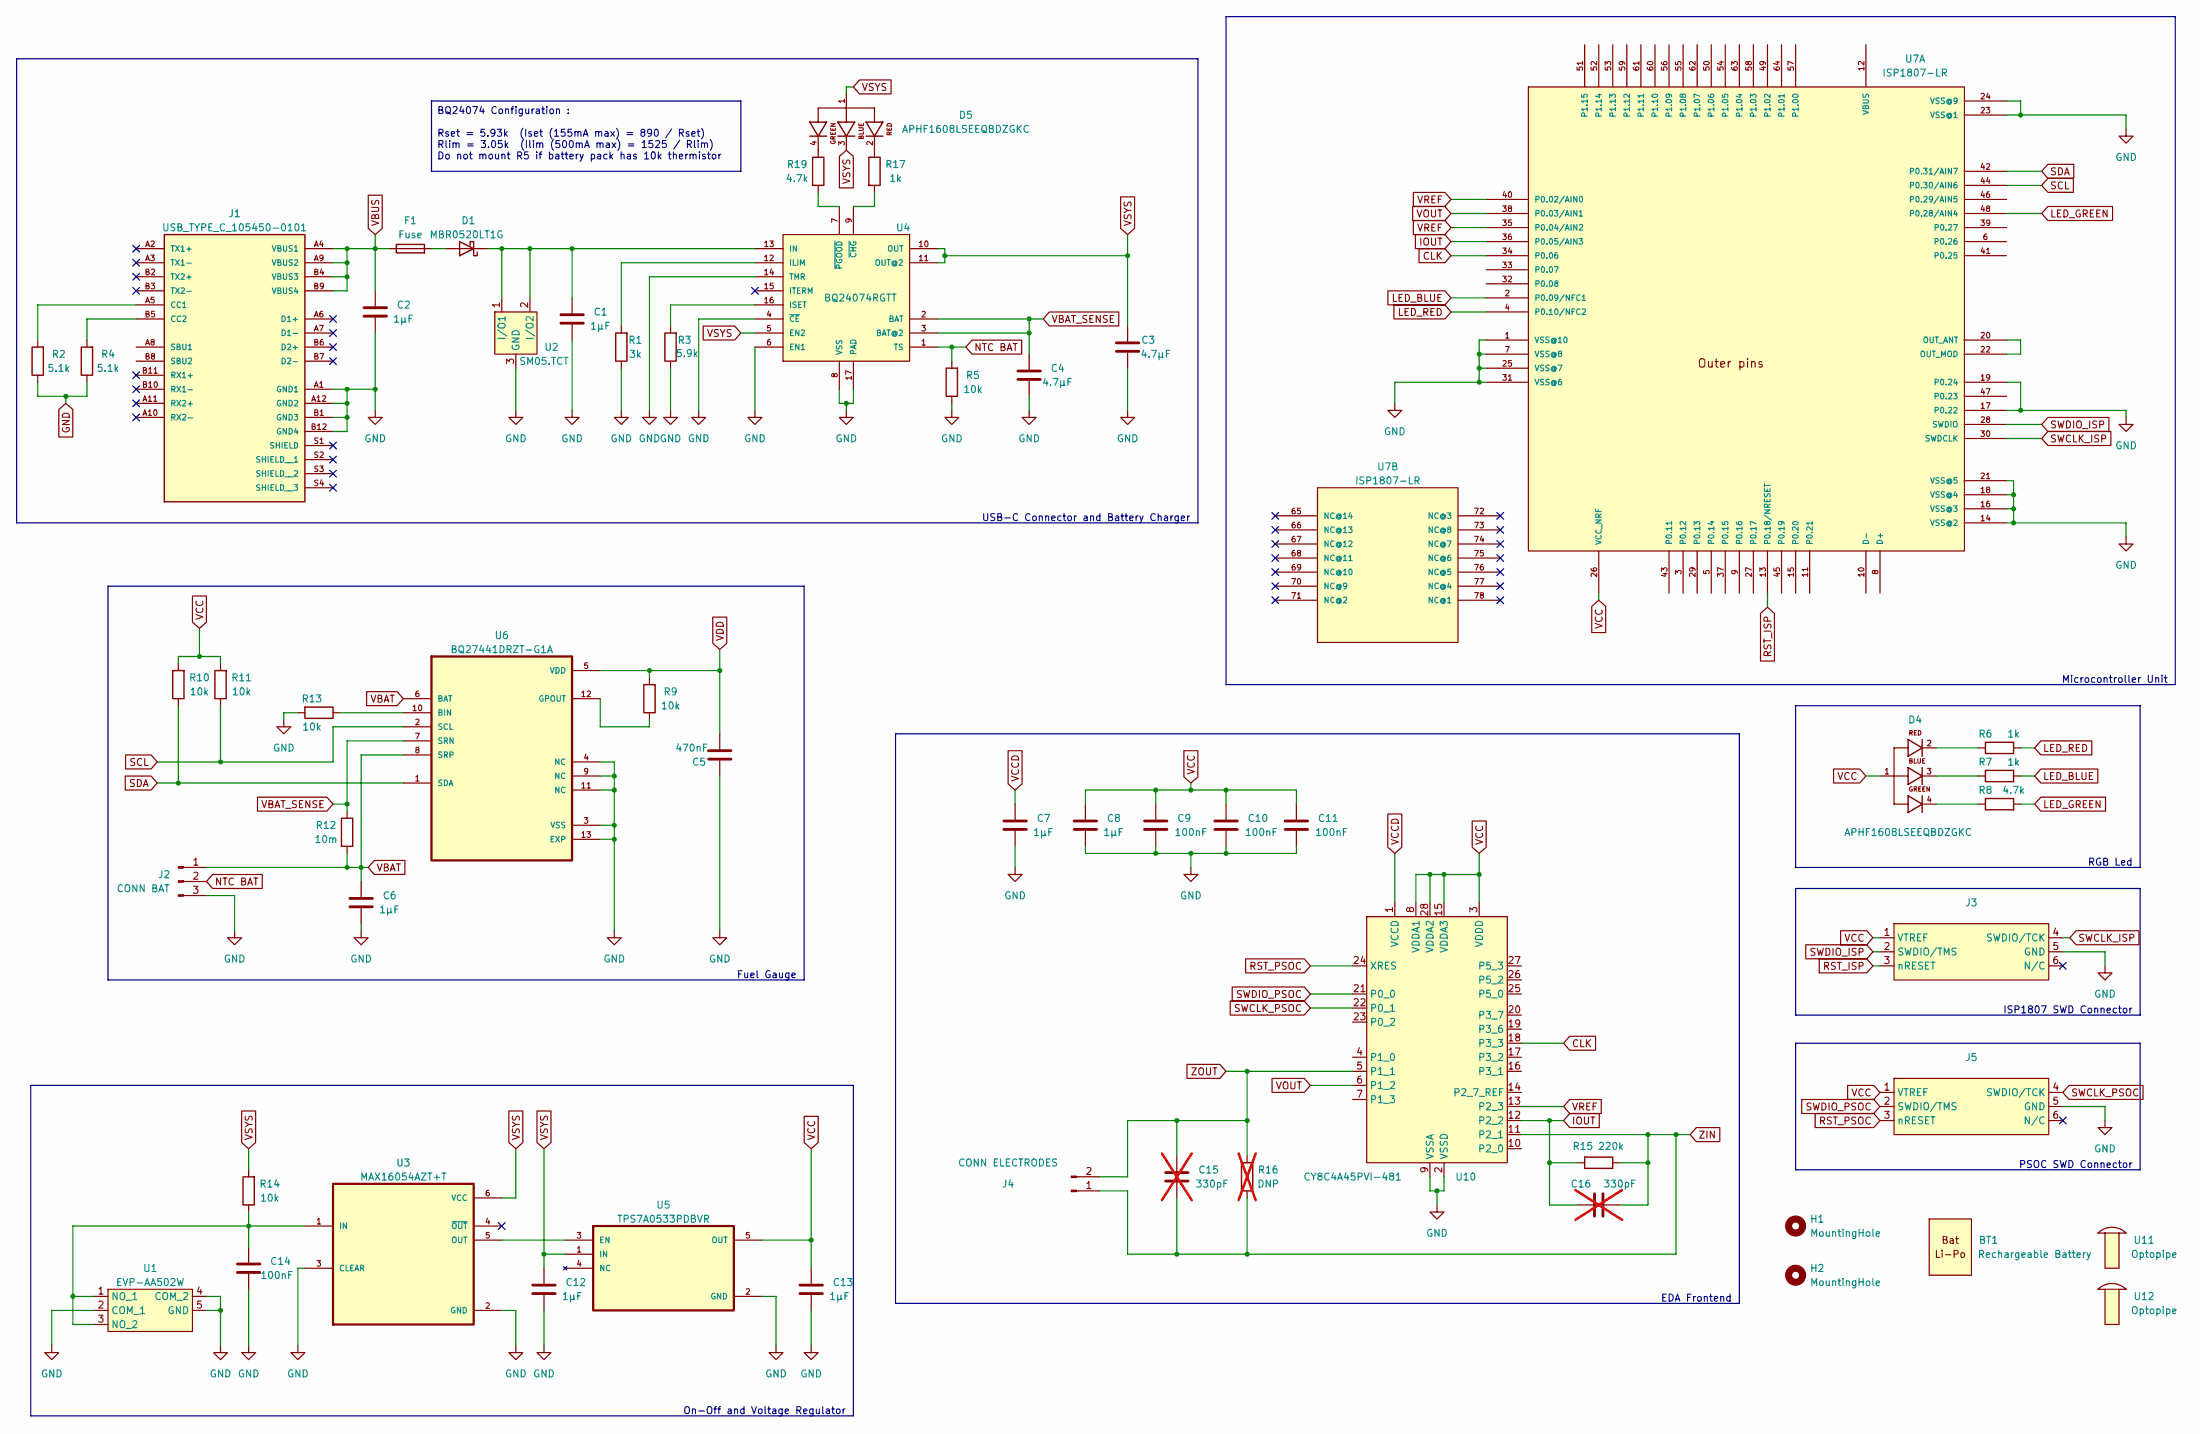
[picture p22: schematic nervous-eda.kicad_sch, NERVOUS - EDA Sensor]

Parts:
BT1: BATT LI-PO 3.7V 165MAH; Manufacturer Part Number LP-402025-1S-3
C1, C2, C6, C7, C8, C12, C13: CAP CER 1UF 10V X5R 0402; C_0402_1005Metric; Manufacturer Part Number CC0402KRX5R6BB105
C3, C4: CAP CER 4.7UF 6.3V X5R 0402; C_0402_1005Metric; Manufacturer Part Number CC0402KRX5R5BB475
C5: CAP CER 0.47UF 10V X5R 0402; C_0402_1005Metric; Manufacturer Part Number CC0402KRX5R6BB474
C9, C10, C11, C14: CAP CER 0.1UF 16V X7R 0402; C_0402_1005Metric; Manufacturer Part Number CC0402JRX7R7BB104
C15, C16: CAP CER 330pF 50V C0G / NP0 0805 MCMT; C_0805_2012Metric; Manufacturer Part Number MCMT21N331F500CT; not fitted
D1: DIODE SCHOTTKY 20V 500MA SOD123; D_SOD-123; Manufacturer Part Number STPS0520Z
D4, D5: LED RGB CLEAR 4SMD; APHF1608LSEEQBDZGKC; Manufacturer Part Number APHF1608LSEEQBDZGKC
F1: PTC RESET FUSE 16V 500MA 1210; Fuse_1210_3225Metric; Manufacturer Part Number 0ZCH0050FF2G
H1, H2: MountingHole; MountingHole_2mm
J1: CONN RCP USB3.1 TYPEC 24P SMD RA; USB_TYPE_C_105450-0101; Manufacturer Part Number 105450-0101
J2: MOLEX 53048-0310; CONN_BAT_53048-0310; Manufacturer Part Number 53048-0310
J3, J5: TC2030-MCP-NL
J4: CONN HEADER R/A 4POS 2.54MM; PinHeader_1x02_P2.54mm_Horizontal; Manufacturer Part Number 77315-118-04LF
R1: RES SMD 3K OHM 1% 1/16W 0402; R_0402_1005Metric; Manufacturer Part Number AC0402FR-073KL
R2, R4: RES 5.1K OHM 0.5% 1/10W 0402; R_0402_1005Metric; Manufacturer Part Number ERJ-U2RD5101X
R3: RES 5.9K OHM 1% 1/16W 0402; R_0402_1005Metric; Manufacturer Part Number RC0402FR-075K9L
R5, R9, R10, R11, R13, R14: RES 10K OHM 1% 1/16W 0402; R_0402_1005Metric; Manufacturer Part Number RC0402FR-0710KL
R6, R7, R17: RES 1K OHM 1% 1/16W 0402; R_0402_1005Metric; Manufacturer Part Number RC0402FR-071KL
R8, R19: RES 4.7K OHM 1% 1/16W 0402; R_0402_1005Metric; Manufacturer Part Number RC0402FR-074K7L
R12: RES 0.01 OHM 1% 1/10W 0603; R_0603_1608Metric; Manufacturer Part Number RL0603FR-070R01L
R15: RES Thick Film, 220kΩ, 1%, 0.125W, 100ppm/°C, 0805; R_0805_2012Metric; Manufacturer Part Number RC0805FR-07220KL
R16: RES Thick Film, 220kΩ, 1%, 0.125W, 100ppm/°C, 0805; R_0805_2012Metric; Manufacturer Part Number RC0805FR-07220KL; not fitted
U1: SWITCH TACTILE SPST-NO 0.02A 15V; EVP-AA502W; Manufacturer Part Number EVP-AA502W
U2: TVS Diode WE-TVS-Standard, VRWM=5.0V; SM05.TCT; Manufacturer Part Number SM05.TCT
U3: IC INTFACE SPECIALIZED TSOT23-6; MAX16054AZT+T; Manufacturer Part Number MAX16054AZT+T
U4: IC BATT CHG LI-ION 1CELL 16QFN; BQ24074RGTx; Manufacturer Part Number BQ24074RGTT
U5: IC REG LINEAR 3.3V 200MA SOT23-5; TPS7A0533PDBVR; Manufacturer Part Number TPS7A0533PDBVR
U6: IC BATT FUEL GAUGE LICOO2 12SON; BQ27441DRZR-G1A; Manufacturer Part Number BQ27441DRZR-G1A
U7: RF TXRX MODULE BT TRACE ANT SMD; ISP1807-LR; Manufacturer Part Number ISP1807-LR-RS
U10: IC MCU 32BIT 32KB FLASH 28SSOP; CY8C4A45PVI-481; Manufacturer Part Number CY8C4A45PVI-481
U11, U12: LIGHTPIPE PNL MT CONVEX 0.250"; Manufacturer Part Number 515-1302-0250F

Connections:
CLK: U7.34 (P0.06), U10.18 (P3_3)
GND: C1.2, C2.2, C3.1, C4.2, C5.2, C6.2, C7.2, C8.2, C9.2, C10.2, C11.2, C12.2, C13.2, C14.2, J1.A1 (GND1), J1.A12 (GND2), J1.B1 (GND3), J1.B12 (GND4), J2.3, J3.5 (GND), J5.5 (GND), R1.1, R2.1, R3.1, R4.1, R5.1, R13.2, U1.2 (COM_1), U1.4 (COM_2), U1.5 (GND), U2.3 (GND), U3.2 (GND), U3.3 (CLEAR), U4.4 (~CE), U4.6 (EN1), U4.8 (VSS), U4.14 (TMR), U4.17 (PAD), U5.2 (GND), U6.3 (VSS), U6.4 (NC), U6.9 (NC), U6.11 (NC), U6.13 (EXP), U7.1 (VSS@10), U7.7 (VSS@8), U7.14 (VSS@2), U7.16 (VSS@3), U7.17 (P0.22), U7.18 (VSS@4), U7.19 (P0.24), U7.21 (VSS@5), U7.23 (VSS@1), U7.24 (VSS@9), U7.25 (VSS@7), U7.31 (VSS@6), U10.2 (VSSD), U10.9 (VSSA)
IOUT: C16.1, R15.2, U7.36 (P0.05/AIN3), U10.12 (P2_2)
LED_BLUE: R7.2, U7.2 (P0.09/NFC1)
LED_GREEN: R8.2, U7.48 (P0.28/AIN4)
LED_RED: R6.2, U7.4 (P0.10/NFC2)
NTC BAT: J2.2, R5.2, U4.1 (TS)
unnamed: D1.2 (A), F1.2
unnamed: C1.1, D1.1 (K), U2.1 (I/O1), U2.2 (I/O2), U4.13 (IN)
unnamed: D4.2, R6.1
unnamed: D4.3, R7.1
unnamed: D4.4, R8.1
unnamed: D5.2, R17.1
unnamed: D5.4, R19.1
unnamed: J1.A5 (CC1), R2.2
unnamed: J1.B5 (CC2), R4.2
unnamed: C14.1, R14.1, U1.1 (NO_1), U1.3 (NO_2), U3.1 (IN)
unnamed: U3.5 (OUT), U5.3 (EN)
unnamed: R1.2, U4.12 (ILIM)
unnamed: R3.2, U4.16 (ISET)
unnamed: R17.2, U4.9 (~CHG)
unnamed: R19.2, U4.7 (~PGOOD)
unnamed: R13.1, U6.10 (BIN)
unnamed: R9.1, U6.12 (GPOUT)
unnamed: U7.20 (OUT_ANT), U7.22 (OUT_MOD)
RST_ISP: J3.3 (nRESET), U7.13 (P0.18/NRESET)
RST_PSOC: J5.3 (nRESET), U10.24 (XRES)
SCL: R11.1, U6.2 (SCL), U7.44 (P0.30/AIN6)
SDA: R10.1, U6.1 (SDA), U7.42 (P0.31/AIN7)
SWCLK_ISP: J3.4 (SWDIO/TCK), U7.30 (SWDCLK)
SWCLK_PSOC: J5.4 (SWDIO/TCK), U10.22 (P0_1)
SWDIO_ISP: J3.2 (SWDIO/TMS), U7.28 (SWDIO)
SWDIO_PSOC: J5.2 (SWDIO/TMS), U10.21 (P0_0)
VBAT: C6.1, J2.1, R12.2, U6.6 (BAT), U6.8 (SRP)
VBAT_SENSE: C4.1, R12.1, U4.2 (BAT), U4.3 (BAT@2), U6.7 (SRN)
VBUS: C2.1, F1.1, J1.A4 (VBUS1), J1.A9 (VBUS2), J1.B4 (VBUS3), J1.B9 (VBUS4)
VCC: C8.1, C9.1, C10.1, C11.1, C13.1, D4.1, J3.1 (VTREF), J5.1 (VTREF), R10.2, R11.2, U5.5 (OUT), U7.26 (VCC_NRF), U10.3 (VDDD), U10.8 (VDDA1), U10.15 (VDDA3), U10.28 (VDDA2)
VCCD: C7.1, U10.1 (VCCD)
VDD: C5.1, R9.2, U6.5 (VDD)
VOUT: U7.38 (P0.03/AIN1), U10.6 (P1_2)
VREF: U7.35 (P0.04/AIN2), U7.40 (P0.02/AIN0), U10.13 (P2_3)
VSYS: C3.2, C12.1, D5.1, D5.3, R14.2, U3.6 (VCC), U4.5 (EN2), U4.10 (OUT), U4.11 (OUT@2), U5.1 (IN)
ZIN: C15.2, C16.2, J4.1, R15.1, R16.1, U10.11 (P2_1)
ZOUT: C15.1, J4.2, R16.2, U10.5 (P1_1)

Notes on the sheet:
Fuel Gauge
On-Off and Voltage Regulator
RGB Led
ISP1807 SWD Connector
Microcontroller Unit
EDA Frontend
PSOC SWD Connector
USB-C Connector and Battery Charger
BQ24074 Configuration : Rset = 5.93k (Iset (155mA max) = 890 / Rset) Rlim = 3.05k (Ilim (500mA max) = 1525 / Rlim) Do not mount R5 if battery pack has 10k thermistor

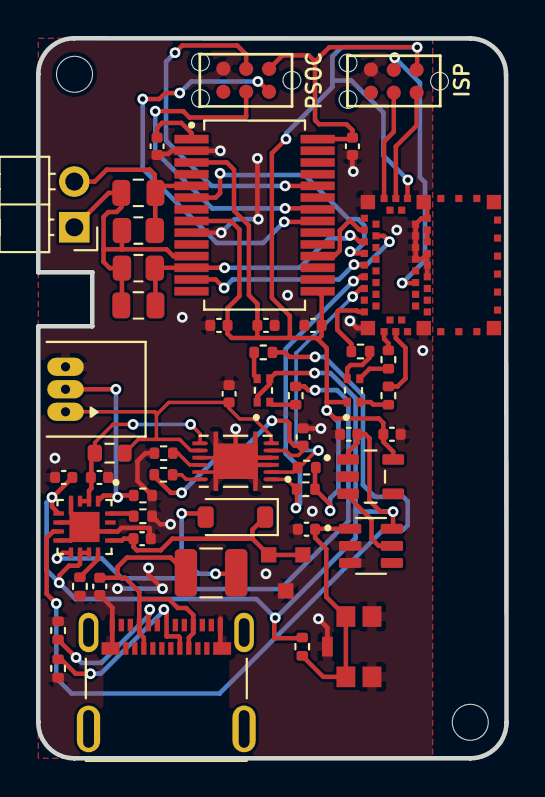
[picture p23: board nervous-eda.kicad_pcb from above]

Board: 2 copper layers, 26.0 x 40.0 mm, 53 parts (0 on the bottom side), 44 nets.

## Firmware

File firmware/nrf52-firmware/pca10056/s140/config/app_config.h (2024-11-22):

/****************************************************************
 * Project: RENFORCE EDA FIRMWARE
 * Module: SDK CONFIGURATION
 *
 *---------------------------------------------------------------
 * @brief SDK configuration overrides for  firmware
 *
 *---------------------------------------------------------------
 * Copyright (c) 2023 INL - INSA LYON
 ****************************************************************/

#ifndef APP_CONFIG_H_
#define APP_CONFIG_H_

/*** ALTERNATIVE DEVKIT CONFIGURATION ***/

/*** LOGGER ***/

#define NRF_LOG_ENABLED                         1
#define NRF_LOG_BACKEND_RTT_ENABLED             1
#define NRF_LOG_BACKEND_RTT_TEMP_BUFFER_SIZE    128
#define NRF_LOG_DEFAULT_LEVEL                   4       /**< 0 => Off; 1 => Error; 2 => Warning; 3 => Info; 4 => Debug */
#define NRF_LOG_USES_COLORS                     1
#define NRF_LOG_BUFSIZE                         4096

/*** BLUETOOTH ***/

#define NRF_SDH_BLE_VS_UUID_COUNT               2
#define BLE_NUS_ENABLED                         1
#define BLE_DFU_ENABLED                         1
#define BLE_BAS_ENABLED                         1
#define BLE_DIS_ENABLED                         1
#define NRF_SDH_BLE_SERVICE_CHANGED             1
#define NRF_DFU_BLE_BUTTONLESS_SUPPORTS_BONDS   0
#define NRF_PWR_MGMT_CONFIG_AUTO_SHUTDOWN_RETRY 1
// Seems to be increased from 1408 (default) for additionnal characteristics
// WARNING : SD RAM size must be increased in linker size by same amount
#define NRF_SDH_BLE_GATTS_ATTR_TAB_SIZE         1440 //1408

/*** APPLICATION MODULE USED ***/

#define NRF_PWR_MGMT_ENABLED                    1
#define APP_SCHEDULER_ENABLED                   1
#define APP_TIMER_ENABLED                       1
#define GPIOTE_ENABLED                          1
#define PPI_ENABLED                             1
#define PWM_ENABLED                             1
#define SPI_ENABLED                             0
#define RTC_ENABLED                             1
#define SAADC_ENABLED                           1
#define TIMER_ENABLED                           1
#define TWI_ENABLED                             1

/*** APP TIMER ***/
#define APP_TIMER_CONFIG_RTC_FREQUENCY          0       /**< 0 => 32768 Hz; 1 => 16384 Hz; 3 => 8192 Hz; 7 => 4096 Hz; 15 => 2048 Hz; 31 => 1024 Hz */
#define APP_TIMER_CONFIG_IRQ_PRIORITY           6       /**< 2 (highest), 3, 6 or 7 (lowest) app priorities */
#define APP_TIMER_CONFIG_OP_QUEUE_SIZE          100

/*** RGB LED CONFIGURATION ***/
#define PWM0_ENABLED                            1
#define RGB_PWM_INSTANCE                        0       /**< PWM instance index */

/*** EDA AFE CONFIGURATION ***/
#define TIMER1_ENABLED                          1
#define EDA_CLK_TIMER_INSTANCE                  1

/*** FUEL GAUGE ***/
#define TWI0_ENABLED                            1
#define TWI0_USE_EASY_DMA                       1

/*** CALENDAR CONFIGURATION ***/
#define RTC2_ENABLED                            1
#define CAL_RTC_INSTANCE                        2       /**< Calendar RTC instance index. */

/*** BOARD GPIOS ***/
#define RGB_LED_RED_PIN                         10                      /**< Active Low */
#define RGB_LED_GREEN_PIN                       28                      /**< Active Low */
#define RGB_LED_BLUE_PIN                        9                       /**< Active Low */
#define EDA_CLK_PIN                             6
#define EDA_VOUT_ANALOG_INPUT                   NRF_SAADC_INPUT_AIN1    /**< P0.03 */
#define EDA_IOUT_ANALOG_INPUT                   NRF_SAADC_INPUT_AIN3    /**< P0.05 */
#define EDA_VREF_ANALOG_INPUT                   NRF_SAADC_INPUT_AIN0    /**< P0.02 */
#define FGA_I2C_SDA_PIN                         31
#define FGA_I2C_SCL_PIN                         30

#endif /* APP_CONFIG_H_ */

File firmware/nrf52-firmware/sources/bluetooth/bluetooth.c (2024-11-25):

/****************************************************************
 * Project: RENFORCE EDA FIRMWARE
 * Module: BLUETOOTH
 *
 *---------------------------------------------------------------
 * @brief Bluetooth module source file
 *
 * Implements mandatory services and characteristics for a HRS
 * profile (GAP, DI, HRS, BAS and NRF BLE UART)
 * Provides convenient API to start/stop advertising, update GATT
 * attributes and manage bonded devices.
 *
 * Dependencies : None
 *
 *---------------------------------------------------------------
 * Copyright (c) 2023 INL - INSA LYON
 ****************************************************************/

 /*
 * Included files
 */

/* Standard C library includes */
#include <stdint.h>
#include <stdlib.h>

/* NRF SDK includes */

// Macro APP_TIMER_TICKS
#include "app_timer.h"

// Generic BLE includes
#include "ble_advertising.h"
#include "ble_conn_params.h"
#include "ble_conn_state.h"

// BLE services includes
#include "ble_dis.h"
#include "ble_bas.h"
#include "ble_nus.h"
#include "ble_dfu.h"

// Other NRF BLE includes
#include "nrf_ble_gatt.h"
#include "nrf_ble_lesc.h"
#include "nrf_ble_qwr.h"
#include "nrf_dfu_settings.h"

// Macro for bootloader skipping CRC check at reboot
#include "nrf_bootloader_info.h"

// Log console
#define NRF_LOG_MODULE_NAME BLE
#define NRF_LOG_INFO_COLOR  3
#include "nrf_log.h"
NRF_LOG_MODULE_REGISTER();

// Power management module for DFU reboot
#include "nrf_power.h"
#include "nrf_pwr_mgmt.h"

// Soft device
#include "nrf_sdh.h"

// Bonding handlings
#include "peer_manager.h"
#include "peer_manager_handler.h"

/* Application includes */
#include "bluetooth.h"

/*
 * Local constants
 */

#define DEVICE_NAME "EDA"                                                   /**< Name of device. Will be included in the advertising data. */
#define MANUFACTURER_NAME "INL - INSA Lyon"                                 /**< Manufacturer. Will be passed to Device Information Service. */
#define HARDWARE_REV "1.0"                                                  /**< Hardware version. Will be passed to Device Information Service */
#define FIRMWARE_REV xstr(APP_VERSION_STRING)                               /**< Firmware version. Will be passed to Device Information Service */
#define MODEL "Nervous EDA Sensors"                                         /**< Model name. Will be passed to Device Information Service */

#define APP_ADV_INTERVAL 500 //1000    /**< The advertising interval (in units of 0.625 ms). */
#define APP_ADV_DURATION 30000   /**< The advertising duration in units of 10 milliseconds. */

#define APP_BLE_CONN_CFG_TAG 1  /**< A tag identifying the SoftDevice BLE configuration. */
#define APP_BLE_OBSERVER_PRIO 3 /**< Application's BLE observer priority. You shouldn't need to modify this value. */

#define MIN_CONN_INTERVAL MSEC_TO_UNITS(12, UNIT_1_25_MS) /**< Minimum acceptable connection interval (15 ms). */
#define MAX_CONN_INTERVAL MSEC_TO_UNITS(24, UNIT_1_25_MS) /**< Maximum acceptable connection interval (30 ms). */
#define SLAVE_LATENCY 0                                    /**< Slave latency. */
#define CONN_SUP_TIMEOUT MSEC_TO_UNITS(200, UNIT_10_MS)   /**< Connection supervisory timeout (2 seconds). */

#define FIRST_CONN_PARAMS_UPDATE_DELAY APP_TIMER_TICKS(1500) /**< Time from initiating event (connect or start of notification) to first time sd_ble_gap_conn_param_update is called (5 seconds). */
#define NEXT_CONN_PARAMS_UPDATE_DELAY APP_TIMER_TICKS(1500)  /**< Time between each call to sd_ble_gap_conn_param_update after the first call (30 seconds). */
#define MAX_CONN_PARAMS_UPDATE_COUNT 1                       /**< Number of attempts before giving up the connection parameter negotiation. */

#define LESC_DEBUG_MODE 0 /**< Set to 1 to use LESC debug keys, allows you to use a sniffer to inspect traffic. */

#define SEC_PARAM_BOND 1                               /**< Perform bonding. */
#define SEC_PARAM_MITM 0                               /**< Man In The Middle protection not required. */
#define SEC_PARAM_LESC 1                               /**< LE Secure Connections enabled. */
#define SEC_PARAM_KEYPRESS 0                           /**< Keypress notifications not enabled. */
#define SEC_PARAM_IO_CAPABILITIES BLE_GAP_IO_CAPS_NONE /**< No I/O capabilities. */
#define SEC_PARAM_OOB 0                                /**< Out Of Band data not available. */
#define SEC_PARAM_MIN_KEY_SIZE 7                       /**< Minimum encryption key size. */
#define SEC_PARAM_MAX_KEY_SIZE 16                      /**< Maximum encryption key size. */

#define DEAD_BEEF 0xDEADBEEF /**< Value used as error code on stack dump, can be used to identify stack location on stack unwind. */

#define NUS_SERVICE_UUID_TYPE BLE_UUID_TYPE_VENDOR_BEGIN /**< UUID type for the Nordic UART Service (vendor specific). */

/*
 * Local macros
 */
#define xstr(s) str(s)
#define str(s) #s

/*
 * Public variables
 */
BLE_NUS_DEF(m_nus, NRF_SDH_BLE_TOTAL_LINK_COUNT); /**< Nordic uart service instance. */
BLE_BAS_DEF(m_bas);                               /**< Structure used to identify the battery service. */
NRF_BLE_GATT_DEF(m_gatt);                         /**< GATT module instance. */
NRF_BLE_QWR_DEF(m_qwr);                           /**< Context for the Queued Write module.*/
BLE_ADVERTISING_DEF(m_advertising);               /**< Advertising module instance. */

/*
 * Local types
 */

/*
 * Local variables
 */
static uint8_t      m_adv_mode = BLE_ADV_MODE_IDLE;             /**< Retain advertising mode */
static uint16_t     m_conn_handle = BLE_CONN_HANDLE_INVALID;    /**< Handle of the current connection. */
static pm_peer_id_t m_peer_id;                                  /**< Device reference handle to the current bonded central. */
static ble_uuid_t   m_adv_uuids[] =                             /**< Universally unique service identifiers. */
    {
        //{BLE_UUID_NUS_SERVICE, BLE_UUID_TYPE_VENDOR_BEGIN}
    };
static uint8_t dfu_request = 0;
static uint8_t m_mtu = 27 - OPCODE_LENGTH - HANDLE_LENGTH;
static uint8_t m_phy = BLE_GAP_PHY_1MBPS;

static ble_connection_callback_t    m_connection_event_callback = NULL;     /**< Pointer to user application callback for handling connection events */
static ble_advertising_callback_t   m_advertising_event_callback = NULL;    /**< Pointer to user application callback for handling advertising events */
static ble_uart_rx_callback_t       m_nus_event_callback = NULL;            /**< Pointer to user application callback for handling RX data from BLE UART */

static uint8_t  m_stop_adv_after_disconnect = 0;    /**< Store request for not starting advetising after next BLE disconnection */
static uint8_t  m_stop_adv_after_idle = 0;          /**< Prevent from restarting advertising after timeout */
static uint8_t  m_tx_busy = 0;                      /**< Store if the module is actually sending a buffer through TX nus */
static uint8_t  * m_tx_buffer = NULL;               /**< The buffer being sent */
static uint16_t m_tx_buffer_bytes_left = 0;         /**< The remaining number of bytes to be sent */ 
static uint16_t m_tx_buffer_size = 0;               /**< The total number of bytes to send */
static uint8_t  m_tx_notifications_enabled = 0;     /**< Store if remote suscribed to TX notifications */
static uint8_t  m_bas_notifications_enabled = 0;    /**< Store if remote suscribed to battery level notifications */

/*
 * Local functions
 */

void assert_nrf_callback(uint16_t line_num, const uint8_t *p_file_name);

static void gatt_evt_handler(nrf_ble_gatt_t *p_gatt, nrf_ble_gatt_evt_t const *p_evt);
static void pm_evt_handler(pm_evt_t const *p_evt);
static void on_conn_params_evt(ble_conn_params_evt_t *p_evt);
static void on_adv_evt(ble_adv_evt_t ble_adv_evt);
static void ble_evt_handler(ble_evt_t const *p_ble_evt, void *p_context);
static void nus_data_handler(ble_nus_evt_t *p_evt);
static void ble_dfu_evt_handler(ble_dfu_buttonless_evt_type_t event);

static void ble_stack_init(void);
static void gap_params_init(void);
static void gatt_init(void);
static void advertising_init(void);
static void services_init(void);
static void conn_params_init(void);
static void peer_manager_init();
static void delete_bonds(void);
static void whitelist_set(pm_peer_id_list_skip_t skip);
static void disconnect(uint16_t conn_handle, void *p_context);

static void nus_send_next_packet(void);

static void on_bas_evt(ble_bas_t * p_bas, ble_bas_evt_t * p_evt);

/****************************************************************
 * IMPLEMENTATION
 ****************************************************************/

/*
 * Public functions
 */

/**
 * @brief Initialize GATT server
 */
void BLE_Init()
{
    NRF_LOG_INFO("Init");
    if (nrf_sdh_is_enabled() == false)
    {
    #if(NRF_DFU_BLE_BUTTONLESS_SUPPORTS_BONDS == 1)
        // Initialize the async SVCI interface to bootloader before any interrupts are enabled.
        APP_ERROR_CHECK(ble_dfu_buttonless_async_svci_init());
    #endif

        ble_stack_init();
        gap_params_init();
        gatt_init();
        // Peer manager init must be before services init in case of DFU
        peer_manager_init();
        // Services init must be before advertising init in case of advertising custom service UUIDS
        services_init();
        advertising_init();
        conn_params_init();
    }
}

/**
 * @brief Disable Bluetooth
 */
void BLE_Deinit()
{
    nrf_sdh_disable_request();
}

/**
 * @brief Return true if there is an active connection
 *
 */
bool BLE_IsConnected(void)
{
    return (m_conn_handle != BLE_CONN_HANDLE_INVALID);
}


/**
 * @brief Register a callback to be called when connection / disconnection event
 *
 */
void BLE_SetConnectionCallback(void * callback)
{
    m_connection_event_callback = callback;
}


/**
 * @brief Register a callback to be called when advertising event
 *
 */
void BLE_SetAdvertisingCallback(void * callback)
{
    m_advertising_event_callback = callback;
}

/**
 * @brief Disconnect from active connection
 *
 */
void BLE_Disconnect(void)
{
    ble_conn_state_for_each_connected(disconnect, NULL);
}

/**
 * @brief Function for starting advertising.
 */
void BLE_AdvertisingStart(bool erase_bonds)
{   
    m_stop_adv_after_idle = 1;
    m_stop_adv_after_disconnect = 0;

    if (erase_bonds == true)
    {
        delete_bonds();
        // Advertising is started by PM_EVT_PEERS_DELETE_SUCCEEDED event.
    }
    else
    {
        /* Uncomment this line if you want to secure connection with whitelisting */
        // whitelist_set(PM_PEER_ID_LIST_SKIP_NO_ID_ADDR);

        APP_ERROR_CHECK(ble_advertising_start(&m_advertising, BLE_ADV_MODE_FAST));
    }
}

/**
 * @brief Function for stopping advertising (only if not connected).
 */
void BLE_AdvertisingStop(void)
{
    m_stop_adv_after_idle = 1;
    if (m_conn_handle != BLE_CONN_HANDLE_INVALID)
    {
        m_stop_adv_after_disconnect = 1;
    }
    else
    {
        if (m_adv_mode != BLE_ADV_MODE_IDLE)
        {
            APP_ERROR_CHECK(sd_ble_gap_adv_stop(m_advertising.adv_handle));
            //ble_advertising_start(&m_advertising, BLE_ADV_MODE_IDLE);
        }
    }
}
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

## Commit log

2025-03-20 fix : readjustment of decoupling capacity positioning
    [nervous-eda-B_Cu.gbr, nervous-eda-B_Mask.gbr, nervous-eda-B_Paste.gbr, nervous-eda-B_Silkscreen.gbr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]
2025-03-20 feat: bump to KiCad 9.0.0
    [nervous-eda.kicad_pcb, nervous-eda.kicad_sch]
2025-03-20 fix: export files
    [nervous-eda-B_Cu.gbr, nervous-eda-B_Mask.gbr, nervous-eda-B_Paste.gbr, nervous-eda-B_Silkscreen.gbr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]
2025-03-21 fix: add device name in csv file
2025-04-04 feat: add second history chart for 724 Hz
2025-10-01 fix: [hw] cosmetics, export files and version update
    [nervous-eda-B_Cu.gbr, nervous-eda-B_Mask.gbr, nervous-eda-B_Paste.gbr, nervous-eda-B_Silkscreen.gbr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]

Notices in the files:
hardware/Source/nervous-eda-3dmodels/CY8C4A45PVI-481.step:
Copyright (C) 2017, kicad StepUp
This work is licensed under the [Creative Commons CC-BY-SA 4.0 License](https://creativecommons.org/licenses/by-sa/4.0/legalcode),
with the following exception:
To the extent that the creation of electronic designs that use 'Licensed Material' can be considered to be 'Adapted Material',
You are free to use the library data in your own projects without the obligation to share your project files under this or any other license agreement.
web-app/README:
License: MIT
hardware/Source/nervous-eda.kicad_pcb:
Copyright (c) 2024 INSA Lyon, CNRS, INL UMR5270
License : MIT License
